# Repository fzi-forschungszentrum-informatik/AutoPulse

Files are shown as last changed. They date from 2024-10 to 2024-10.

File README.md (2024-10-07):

# AutoPulse: The ultimate do-it-yourself EMFI automation platform

This project was created researchers at KASTEL and the FZI Forschungszentrum Informatik.
In this repository, you will find the necessary files to build your own EMFI automation platform.

## [Assembly](/assembly/README.md)

This section contains the build instructions, as well as a BOM and the necessary 3D files to build your own EMFI automation platform.
As a note, these instruction are heavily reliant on the use of a specific 3D printer, the Ender 3 S1.
We used this printer because it was widely available, and contains both reliable as well as very affordable components.
It's possible to follow these instructions with a different 3D printer, but you may need to adjust the 3D files accordingly.
Take a look at these requirements when selecting a different 3D printer:

1. UART capable TMC stepper drivers.
   - The Ender 3 S1 uses TMC2208 stepper drivers, which are UART capable.
   - We needed to modify the mainboard slightly to enable UART mode.
2. Dual Z-Axis stepper motors.
   - Some Ender 3 models only have one stepper motor for the Z-Axis, which reduces the Z-Axis consistency across the X-Axis.
3. [klipper](https://klipper3d.org/) compatibility.
4. v-slot rollers on the X and Y-Axis.
   - Other solutions exhibit larger static friction, which will reduce the accuracy during small movements.

## Software

Take a look at the [Readme](pulsecontrol/README.md) in `pulsecontrol`, it details the steps required to install and configure the software part of this project.

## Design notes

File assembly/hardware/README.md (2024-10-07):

# Build Instructions

This section will guide you through the process of assembling the hardware components and the main assembly of the AutoPulse system.

## Dissabling the stock hotend

We are using parts of the stock hotend for our EMFI mount, so we need to remove the stock hotend first, if you've already installed it. If the printer is still in its stock configuration, you can skip this step, as the hotend is already removed.

#TODO Add disassembly instructions

## EMFI Mount Assembly

The EMFI mount is a simple assembly consisting of four parts: the clamp, the mounting plate, and the CR-Touch and camera extensions.
We first need to insert the heat-set inserts into each parts.

A minimum of 12 inserts are required for the assembly, but we recommend using 16 inserts for added stability and functionality.
Take a look at the images below for reference on where to insert the inserts.
Set your soldering iron to a temperature between 180-200°C and use a wide and short soldering tip push in the inserts.

### Mounting Clamp

#### Parts List

- 6x M3x6mm SHCS
- 4x M3 washer
- 12x heat-set insert (minimum 10)
- (printed) clamp

#### Assembly

Install the heat-set inserts into the clamp, take a look at the refercence images for the correct mounting positions.

Carriage Mount Sockets
Mounting Plate Sockets
CR-Touch Mount Sockets

### Mounting Plate

#### Parts List

- 4x heat-set insert (minimum 2)
- (optional) 1x M3x10mm SHCS

#### Assembly

Install the heat-set inserts into the mounting plate, take a look at the refercence images for the correct mounting positions.
The two outer inserts on the bottom of the plate are required for the PCB camera extension, the two other inserts are optional, one is for one additional screw on the PCB camera extension, the other is for the optional M3x10mm screw we use as a zip-tie anchor.

Mounting Plate

### CR-Touch Extension

#### Models

- [Swivel](../models/Touch-Probe/Touch-Probe-Body.step)
- [Mount](../models/Touch-Probe/Touch-Probe-attachment.step)

#### Parts List

- 5x heat-set insert
- 2x M3x6mm SHCS
- 3x M3x10mm SHCS
- 1x M4x16mm SHCS
- 4x 6x3mm Neodym Magnet 

#### Assembly

Install the heat-set inserts into the CR-Touch swivel and mount, take a look at the refercence images for the correct positions.
CR-Touch Swivel HEAT-SET

Next, install the magnets into the appropriate cutouts. Make sure the magnets are aligned to attract each other, as shown in the reference image. The cutouts are tight, so no glue should be necessary to keep them in there. You might need to push them in using a screwdriver. Be carefull to not break the printed part!
CR-Touch Magnets 1
CR-Touch Magnets 2

We are now ready to attach the swivel arm to the mounting bracket. Use the M4 screw and some elbow grease. The swivel arm has enough clearance for it to freely swing around the screw as a pivot, but the mounting bracket screw-hole is designed to be self-tapped by the M4. The clearance is designed for PLA parts, so your milage may vary if you're using a different material. 
CR-Touch Pivot Screw

Now for attaching the CR-Touch. Use the M3x6mm screws to mount the probe to the swivel arm. Guide the cable through the provided hole. It's easier to keep the cable attached to the CR-Touch rather than attaching it once the probe is screwed in.
CR-Touch Probe Attachment
CR-Touch Probe Attachment

Finally, attach the part to the mounting clamp. First insert the heat-set inserts on the front of the mounting clamp, as shown here: 
CR-Touch Mounting Holes

Then attach the part to the clamp with the M3x10mm screws.
CR-Touch Pointing Down
You should now be able to tilt the CR-Touch probe out of the way after the initial sequence is done, which helps with clearance on some target boards.
CR-Touch Tilted Away

### PCB Camera Extension

#TODO Add parts list
#TODO Add assembly instructions

### Probe Camera

For the final assembly of the probe camera, we it's best to have the Raspberry Pi already set-up, as well as all components already connected.
We will then open up the camera view, which simplifies the final alignment of the camera.

#TODO Add parts list
#TODO Add assembly instructions

#### Replacing the stock leveling screws

The default leveling screws are too large for the new probe camera module and will interfere with the movement of the carriage. We have designed a simple replacement part that is easy to print and install.
Screws
Our part uses the same threaded insert as the stock screws. Simply use a soldering iron to heat the insert, pushing it out of the stock screw, and insert it into the new part.
We recommend to only replace the screws on the left side of the printer, as the right side is not impacted by our probe camera module.

## Assembly

#### Parts List

- 6x M3x6mm SHCS
- 4x M3 washer
- 1x stock Creality PCB breakout board
- 1x assembled EMFI mount

#### Assembly

Use two of the M3x6mm screws to attach the PCB breakout board to the mounting assembly.
Place two washers each between the printed part and the PCB breakout board.
Be careful when screwing in the screws, the mounting tabs are fragile.

Line up the assembled EMFI mount with the printer carriate, then screw in the M3x6mm screws.

## Electronics

**WARNING**: The following steps require you to open the electronics compartment of the printer. This will void your warranty. We are not responsible for any damage caused to your printer. If you are not comfortable with these steps, please ask for help from someone who is. Keep the printer unplugged while performing these steps.

### Opening the electronics compartment

1. Lay the printer on its right side. Remove the screen beforehand,
   you won't be needing it in the future.
2. Remove the tool-drawer before trying to remove the bottom panel.
3. Remove the 9 screws from the bottom panel.
4. Remove the bottom panel. Carefully detach the cooling fan cable from the control board before removing the panel completely.

### (Optional) Adding UART support for the TMC2208 stepper drivers

This step is optional, but highly recommended. It will enable UART for the stepper drivers, allowing for higher accuracy and quieter operation.
If you want to do this, follow the instructions in the [Enabling UART for the TMC2208 Stepper Drivers](#part-99999-optional-enabling-uart-for-the-tmc2208-stepper-drivers) section, then return here.
You can also do this step after the initial setup, but it is easier to do it now, while the electronics compartment is already open.

### Wiring

1. Locate the heated-bed cable and thermistor cable. Both are located on the left of the board, labeled as "BED" and "BED TEM" respectively. Take a look at our [wiring diagram](img/wiring-diagram.png) for reference.
2. Use your fingers to remove the hot-glue from the heated-bed cable and the thermistor cable. Try to avoid using metal tools for removing the hot-glue, as you might damage the PCB.
3. Unscrew the terminals of the heated-bed cable and the thermistor cable. You can use a flat-head screwdriver for this.
4. Insert the cables for the probe-LEDs into the terminals previously used for the heated-bed.
   Keep the polarity in mind.
   Test this before before closing the electronics compartment.
5. Use the cable-clip at the top of the aluminium extrusion to secure LED cable.
6. (Optional) While the panel is open, remove the bottom cable clip which usually holds the rainbow cable. Secure the end with the tape that's already holding it down.
7. Note down the exact chip on the control board. We will need this in the future. It should be one of either `STM32F401` or `STM32F103`.
8. Replace the bottom panel and secure it with the 9 screws. Keep in mind to reattach the cooling fan cable to the control board.

### Raspberry Pi

#### Power Supply

We are using the official Raspberry Pi power supply, but it is entirely possible to use one of these [img/variable-power-supply.jpg](variable power supplies) instead. The official power supply is rated at 5.1V and 5.0A. The power supply should be connected to the USB-C port on the Raspberry Pi.

As an alternative, we have also tested the Raspberry Pi with a cheap variable power supply.
This has the advantage of being able to power the Pi with the 24V power supply of the printer, requiring one less power outlet.
The power supply should be connected to the GPIO pins on the Raspberry Pi.
The positive wire should be connected to pin 2 and the negative wire should be connected to pin 6.

#### CSI Camera Cables

Next, you should connect the CSI camera cables to the Raspberry Pi.
The camera cables should be connected to the CSI port on the Raspberry Pi.
The camera cables should be connected to the Raspberry Pi with the black side facing away from the Ethernet port.
The order of the cameras doesn't matter, just route them as fits best with the physical layout of your components.
You can verify both cameras work by running `libcamera-hello -n` in the command line.
There will be two outputs of `Registered camera`, each providing a path to `/dev/media{0,1,2,3}`.
All cameras should be detected out of the box when using the default raspbian image.
Try rebooting you can't connect to the cameras.
Never unplug the cameras while the Raspberry Pi is powered on.
The metal contacts on the ribbon cable can short something during unplugging, which could damage the Raspberry Pi or the Cameras.

#### Connecting the Raspberry Pi to the Printer

Use a USB-A to USB-C cable to connect the Raspberry Pi to the printer. The USB-A side should be connected to the Raspberry Pi and the USB-C side should be connected to the printer.

## Installing Klipper

### Part 0: Installing Docker

We like to use the `printd` service to manage the `klipper` configuration. This will use marginally more resources than a direct deployment of klipper, but comes with advantage of simplified dependency management simple installation.
It does require a working docker installation, so we will start by setting that up.

To do this, follow the instructions at [docs.docker.com/engine/install/debian](https://docs.docker.com/engine/install/debian/#install-using-the-repository).
Then add your user to the `docker` group with `sudo usermod -aG docker $USER`.
You will need to log out and back in for this change to take effect.

### Part 1: Setting up `printd`

1. Clone the repository with `git clone https://github.com/mkuf/prind.git`.
2. Move into the directory with `cd printd`.
3. Register the alias for simplifying the following commands. Run `alias pmake="docker compose -f docker-compose.extra.make.yaml run --rm make"`.
4. Run `pmake menuconfig`.
   Use the arrow keys to navigate the TUI, use the space bar to select and deselect options, and use the enter key to enter sub-menus.
5. Select `Enable extra low-level configuration options`
6. Select `STMMicroelectronics STM32` as your microcontroller architecture.
7. The processor model is the model number you have noted down in the wiring step.
8. If you have the `STM32F401`, select the `64KiB bootloader` offset. If you have the `STM32F103`, select the `28KiB bootloader` offset.
9. Press `q` to exit the menu and `y` to save the configuration.
10. Run `pmake` to build the firmware.
11. The finished firmware will be at `out/klipper.bin`.

#### Copying the configuration

The default location for the `printer.cfg` in `printd` is ... [TODO]: # Add path, update this description

## Part 2: Flashing the Mainboard

1. You should already have the `klipper.bin` from the previous step.
   - If you have the `STM32F103`, move this file to the root of the SD-card that came with the printer.
   - If you have the `STM32F401`, create a subfolder called `STM32F4_UPDATE` and move the file there.
2. With the printer turned off, insert the SD-card into the printer, then turn the printer on.
3. You'll get no feedback as to if you've been successful, but the printer should now be running Klipper.

**Note** If you want to change some settings and flash the firmware again, re-name the `*.bin` to something else. The MCU will not flash the same firmware file again if it has the same name.

Use these images to compare with your settings:

STM32F401
STM32F103

**Note** You are now ready to start using klipper. The next steps are optional, but highly recommended.

## Part 99999: (Optional) Enabling UART for the TMC2208 Stepper Drivers

The default configuration of the steppers on the Ender 3 S1 is tuned for fast and silent movements during prints. We do not care about speed or noise, we want the highest possible accuracy. To achieve this, we will need to enable UART for the TMC2208 stepper drivers.

### Removing the control board

1. Take a picture of the control board, to make reassembly easier.
2. Remove all hot-glue from the connectors, then
3. Disconnect all cables from the board.
4. Remove the five screws holding it in place.
5. Remove the board from the printer.

### Soldering the jumpers

1. Orient the board in such a way that the USB and SD-card slots are on the right side.
2. Locate the stepper drivers, they are on the top of the board, with each having a small heat sink glued to it.
   - Underneath each heat sink are multiple resistors in a row. One of these resistor pads is unpopulated, and this is where we will solder the jumper.
   - The upper pad itself is connected to the resistor to the left of it, which in turn is connected to the UART pin of the stepper driver.
   - We will use this empty pad to solder the jumper, because it gives us a larger target for our soldering iron.
3. Solder a Jumper to the upper pad of the three leftmost stepper drivers. We don't care about the extruder stepper driver, as it is not used in our device.
   - It's possible to use the extruder stepper as a backup, if one of the other steppers is damaged during our modifications.
4. Either crimp a dupont connector to the other end of the jumper, or solder it directly to one of the unused pins for the touch screen. Take a look at the pictures for reference.
5. Update the `printer.cfg` with the correct UART pins. Uncomment the `[tmc2209 stepper_{x|y|z>}` section if you used the same pins as in the pictures.
   - Pins `PB2`, `PB1` and `PA2` of the `STM32F401` are connected to the empty touchscreen-connector on the control board. We chose to use those because of them being in a straight, direct line, making it easier to attach a dupont connector to them.
   - Take a look at the data sheet of your chip if you want to use other pins. Simply use a multimeter to measure for continuity between the legs of the chip and the pins on the board to find the correct ones.
6. Continue with the instructions in the [Wiring](#wiring) section.

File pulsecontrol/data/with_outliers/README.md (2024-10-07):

# Explainations

## 0.01

### DR: Outlier at 276:

The glass measurement stick traversed past the 100mm point, which resets the device measurements from previously skipped steps

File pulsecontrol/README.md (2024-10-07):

# PulseControl

## Development

I found that using the pycharm remote interpreter is the best way to develop on the PI. This way you can use the IDE on your local machine and the code runs on the PI.
Add New Interpreter

Otherwise clone or rsync the code to the PI and run it there.
Make sure the PI has the required dependencies installed:

```bash
rye sync
```

To start the server, run:
```bash
just server-start
```
in the `pulsecontrol` directory.

To start a run with a specific configuration, run:
```bash
just init configuration/<description>/<integrator-name>.json 
just start
```
the description is a directory in the configuration directory and the integrator-name is the name of the integrator in the configuration file.
The integrator needs to have the same name as the python file in the integrators directory.

In the current case, this would be:
```bash
just init configuration/spc/bam.json 
just start
```

This will immediately start the run with the specified configuration.

To stop the server, run:
```bash
just reset
```
or stop the current run in PyCharm.

## Installation

**Note:** This is only required once, on the PI the server is going to run.
```bash
apt install libcap-dev libcamera-dev libksm++-dev libfmt-dev libdrm-dev python3-opencv
```

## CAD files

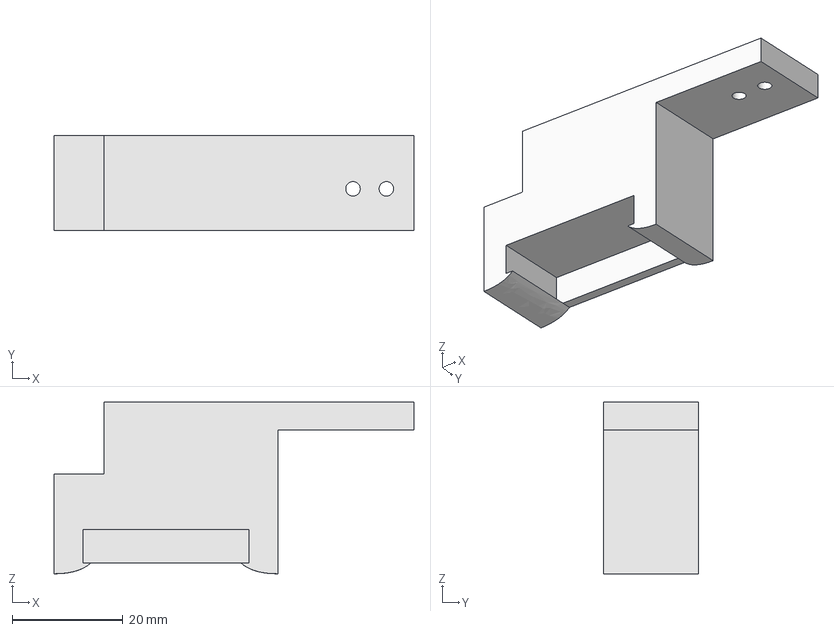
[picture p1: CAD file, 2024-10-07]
docs/assembly/models/Cable-Clip/Cable-Clip.FCStd
65.0 x 17.1 x 31.0 mm

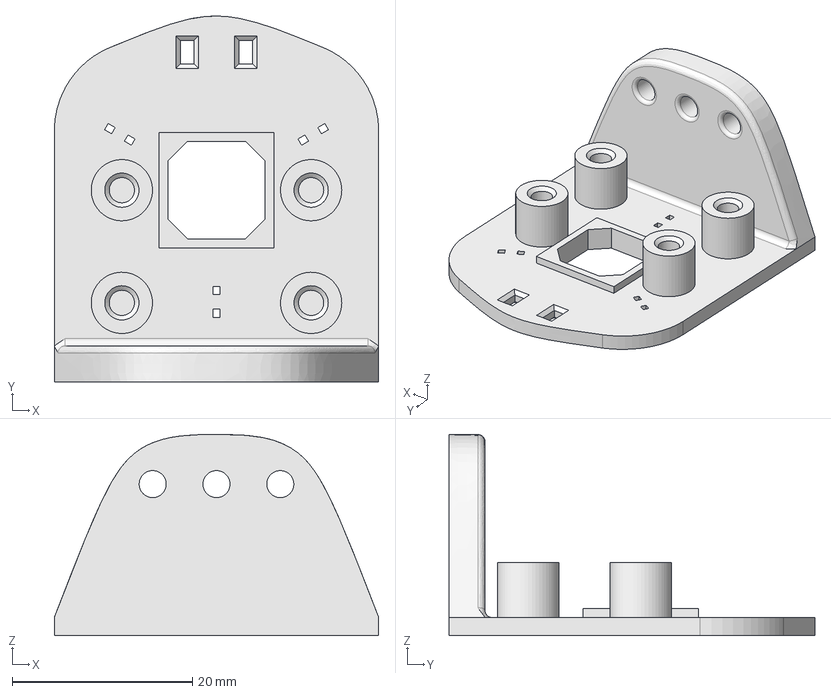
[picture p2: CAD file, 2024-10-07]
docs/assembly/models/PCB Cam/mount.FCStd
36.0 x 40.6 x 22.3 mm

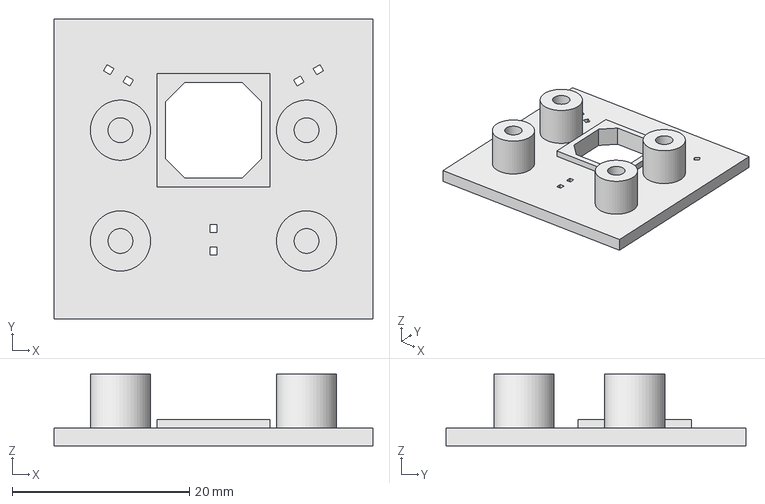
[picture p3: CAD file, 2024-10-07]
docs/assembly/models/Probe Cam/probe-cam.FCStd
36.0 x 33.8 x 8.10 mm

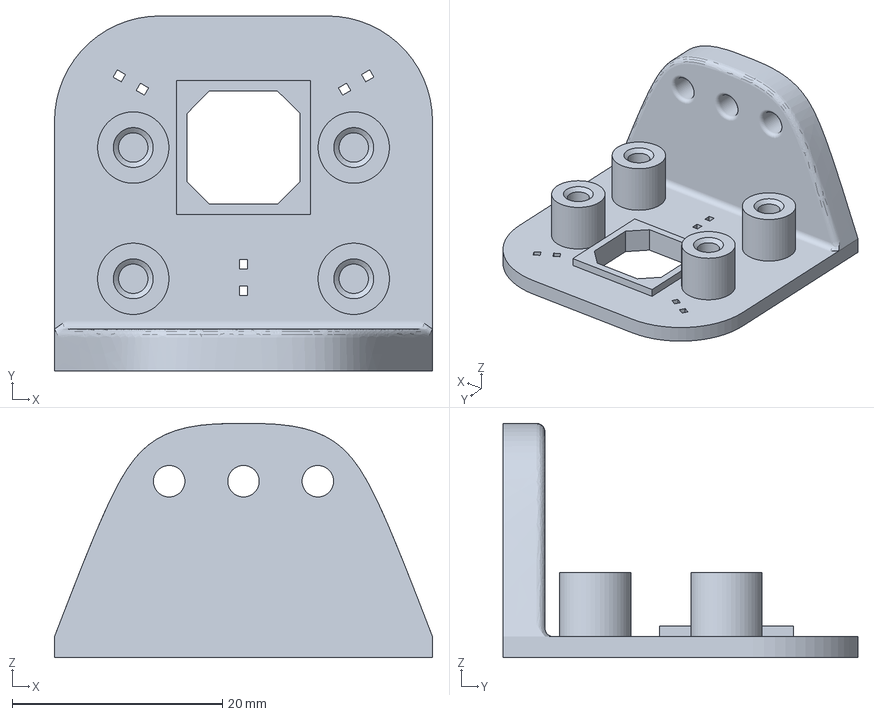
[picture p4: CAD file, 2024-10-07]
docs/assembly/models/PCB Cam/mount-BodyPad003.3mf
36.0 x 33.8 x 22.3 mm

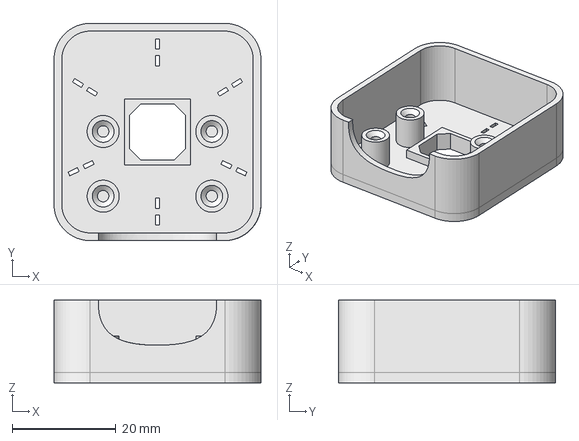
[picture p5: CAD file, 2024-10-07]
docs/assembly/models/Probe Cam/probe-cam2.FCStd
40.0 x 42.0 x 16.0 mm

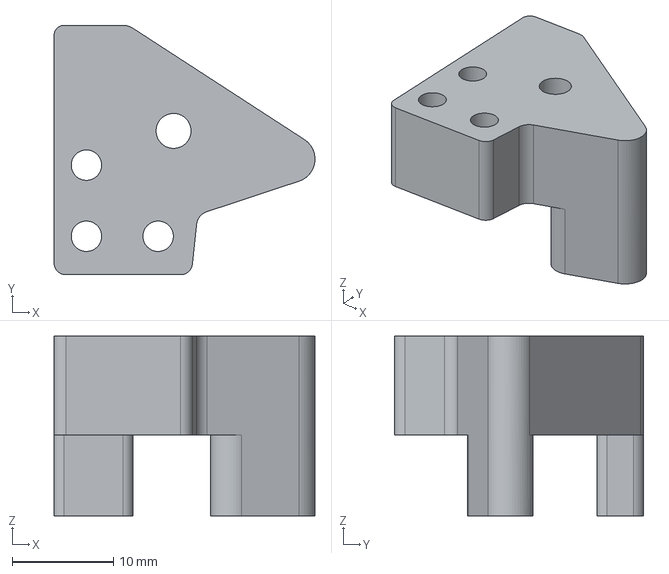
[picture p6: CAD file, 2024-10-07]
docs/assembly/models/Touch-Probe/Touch-Probe-attachment.step
25.8 x 24.6 x 17.7 mm

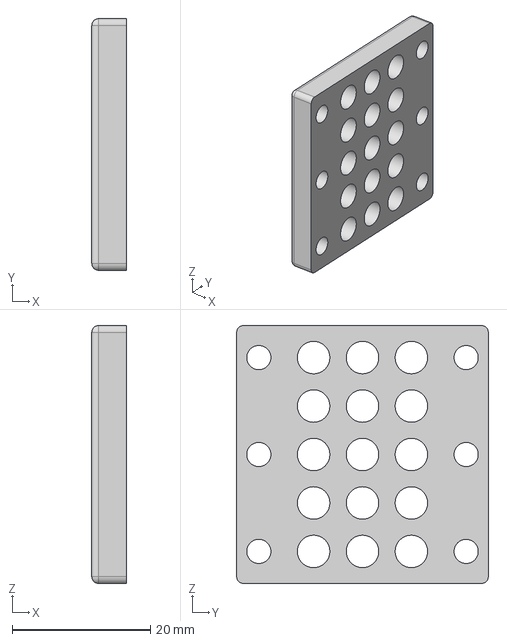
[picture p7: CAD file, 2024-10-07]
docs/assembly/models/PCB Cam/extra.FCStd
5.00 x 36.4 x 37.4 mm

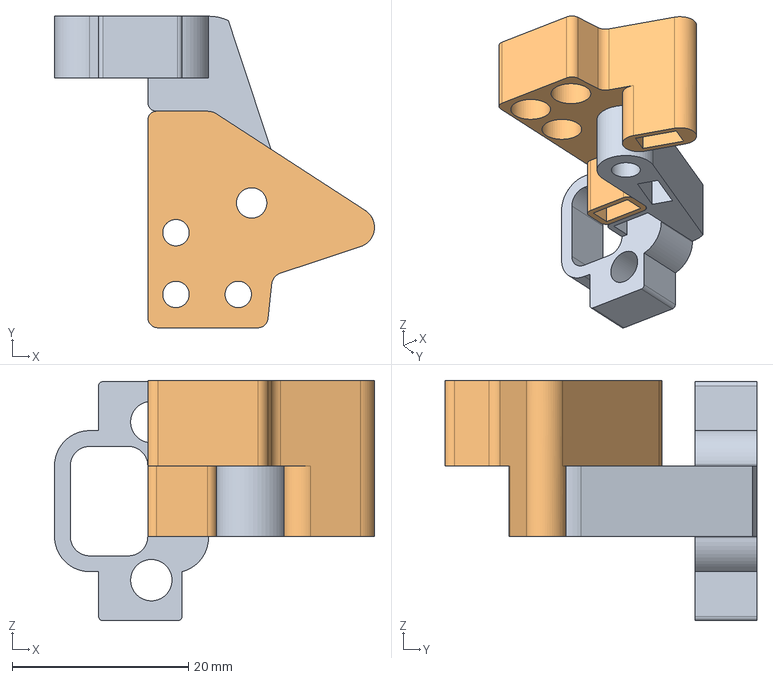
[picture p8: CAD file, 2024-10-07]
docs/assembly/models/Touch-Probe/Touch-Probe.FCStd
36.4 x 35.4 x 27.3 mm
attachment

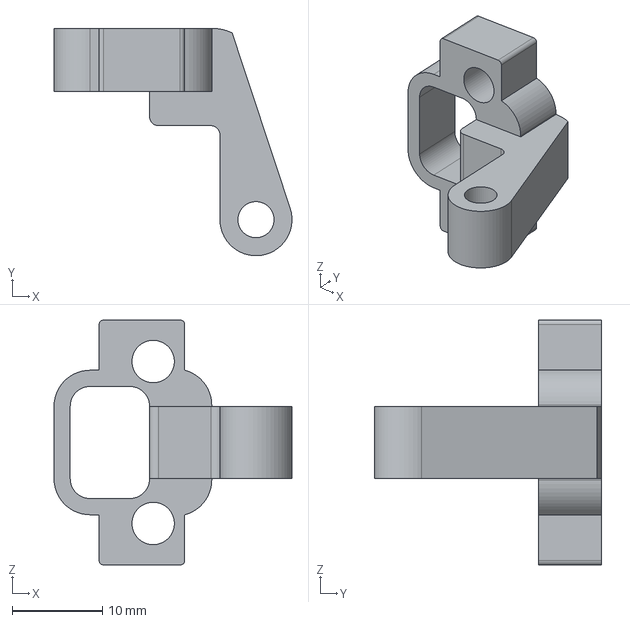
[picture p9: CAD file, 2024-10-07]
docs/assembly/models/Touch-Probe/Touch-Probe-Body.step
26.4 x 25.2 x 27.2 mm

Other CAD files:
docs/assembly/models/Touch-Probe/magnet_attachment_horizontal.FCStd
docs/assembly/models/Probe Cam/probe-cam2-BodyPocket003.3mf
docs/assembly/models/PCB Cam/mount-BodyChamfer001.step
docs/assembly/models/PCB Cam/mount-BodyChamfer001.iges

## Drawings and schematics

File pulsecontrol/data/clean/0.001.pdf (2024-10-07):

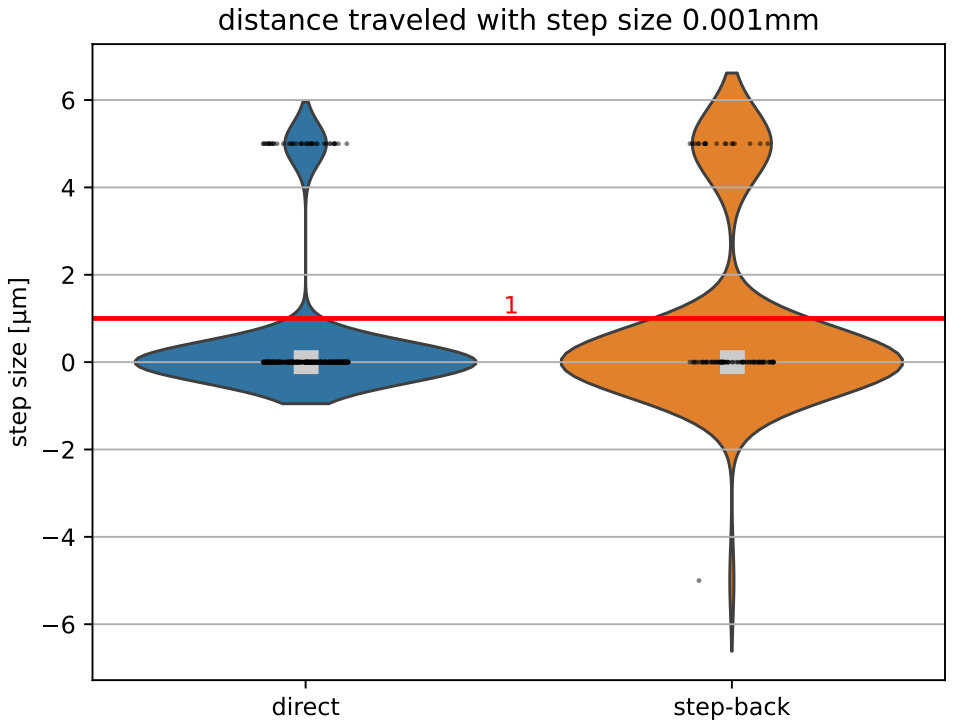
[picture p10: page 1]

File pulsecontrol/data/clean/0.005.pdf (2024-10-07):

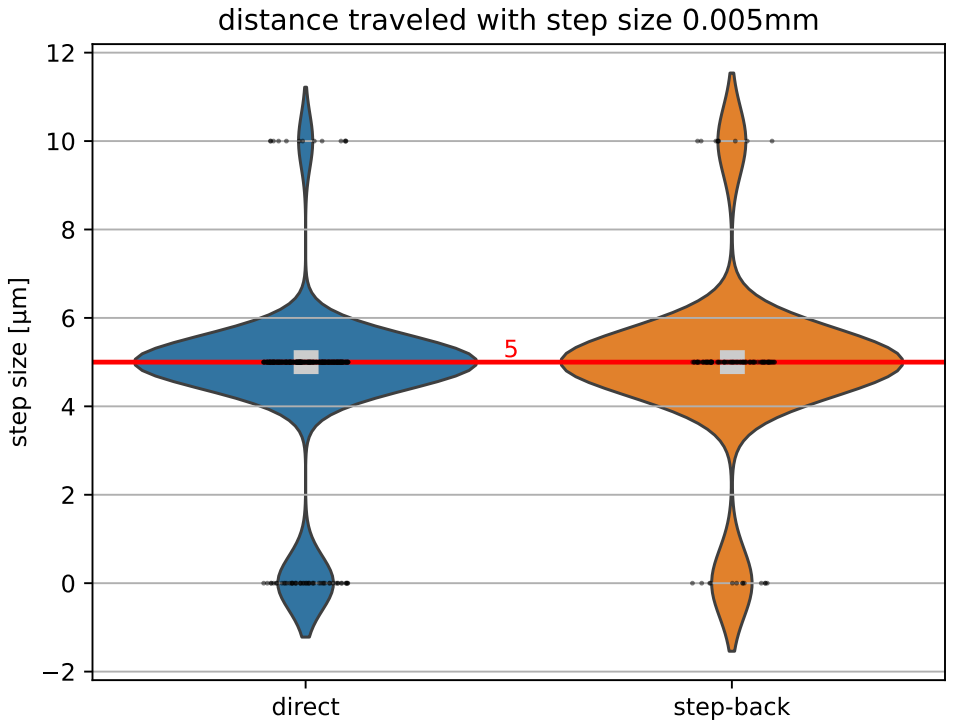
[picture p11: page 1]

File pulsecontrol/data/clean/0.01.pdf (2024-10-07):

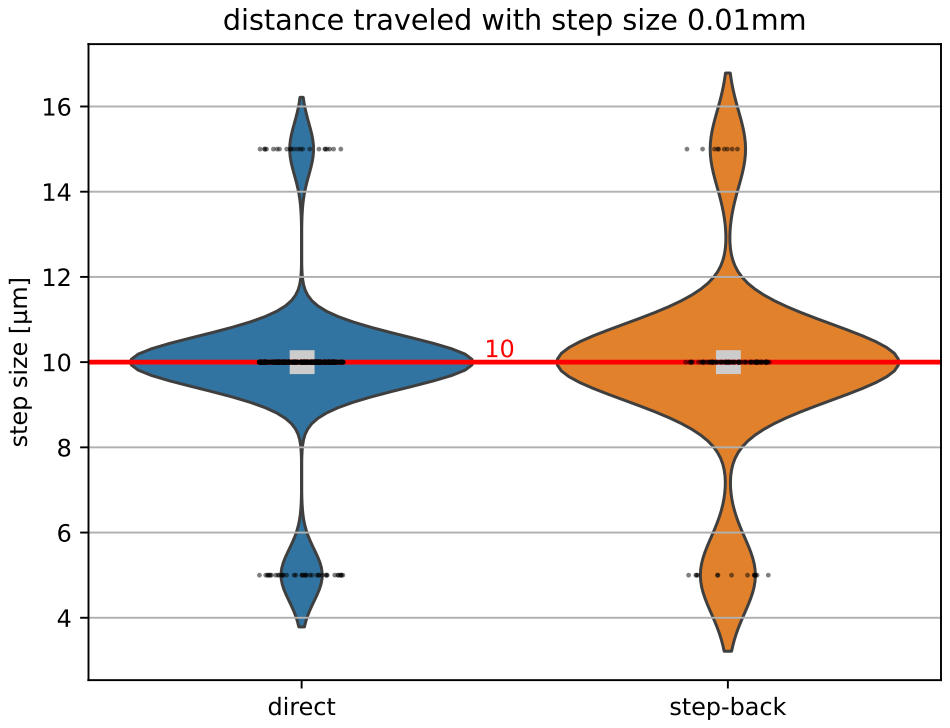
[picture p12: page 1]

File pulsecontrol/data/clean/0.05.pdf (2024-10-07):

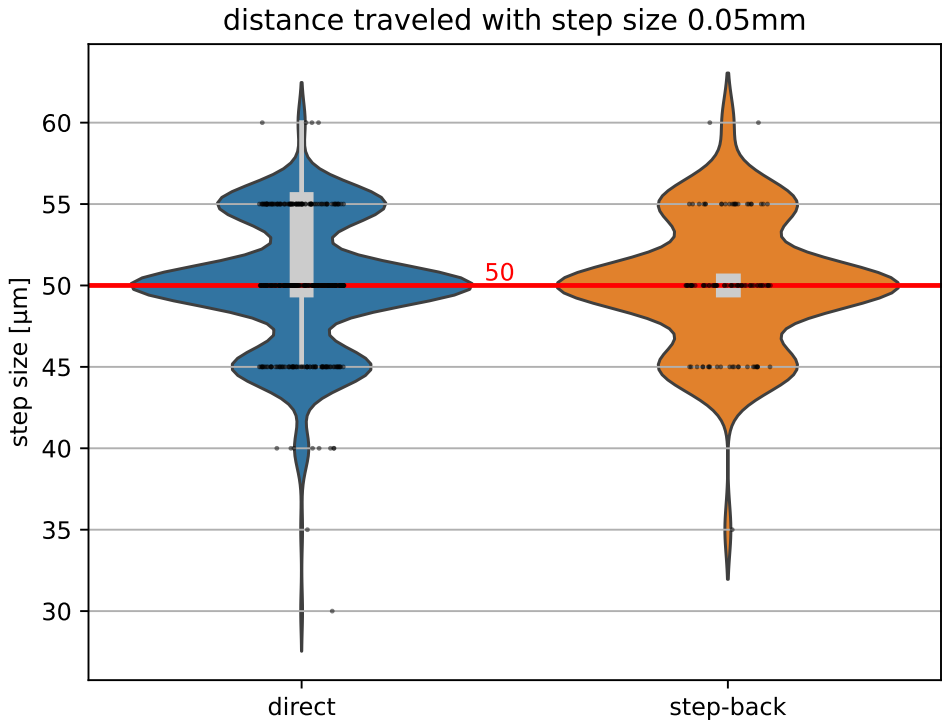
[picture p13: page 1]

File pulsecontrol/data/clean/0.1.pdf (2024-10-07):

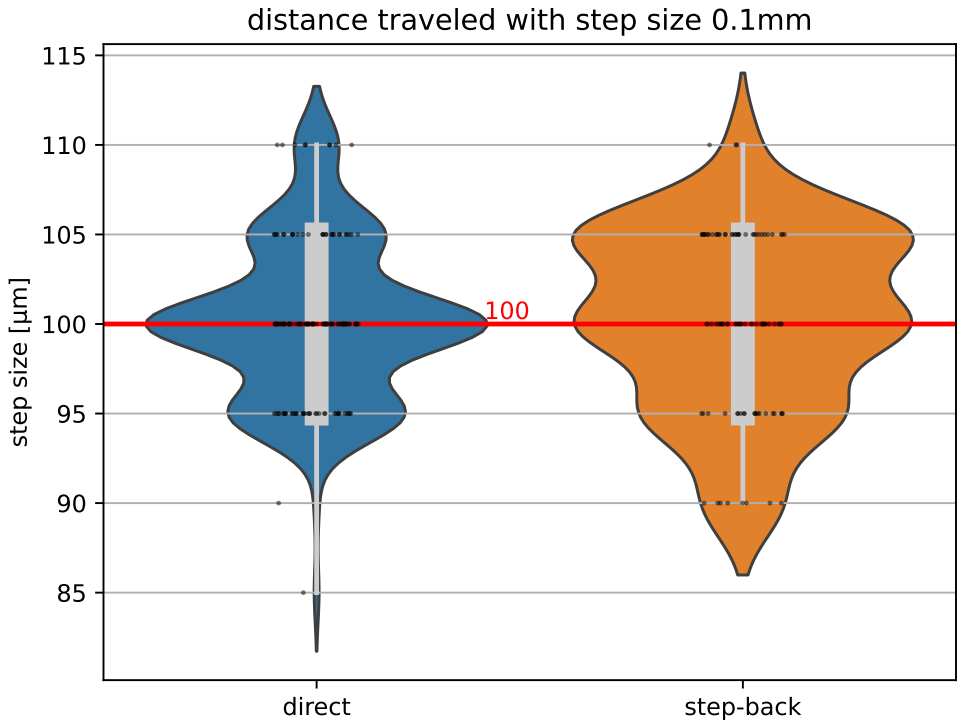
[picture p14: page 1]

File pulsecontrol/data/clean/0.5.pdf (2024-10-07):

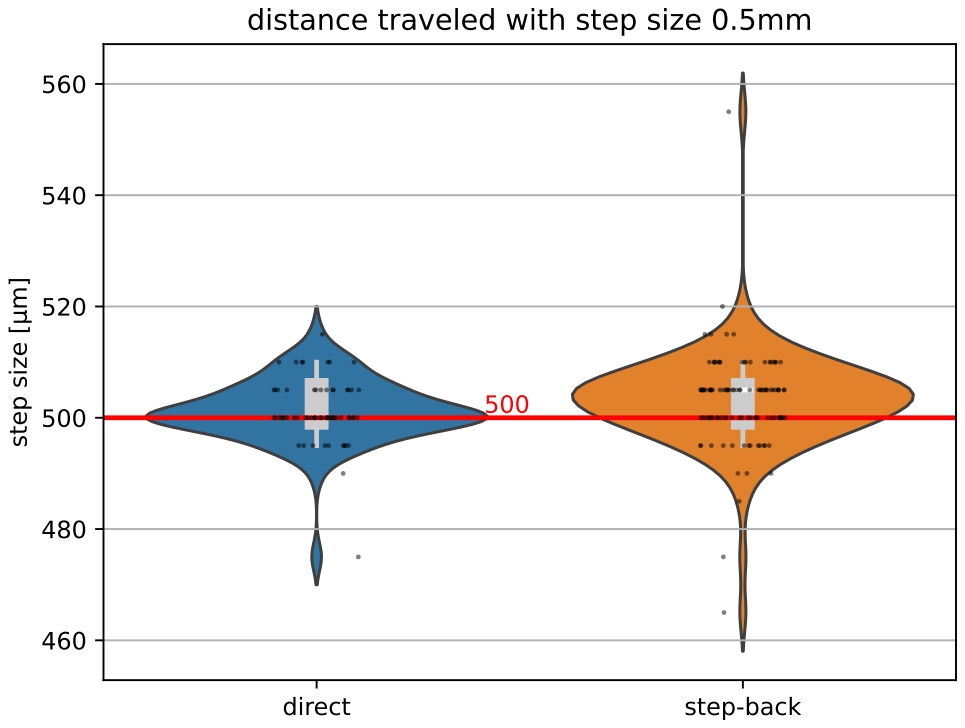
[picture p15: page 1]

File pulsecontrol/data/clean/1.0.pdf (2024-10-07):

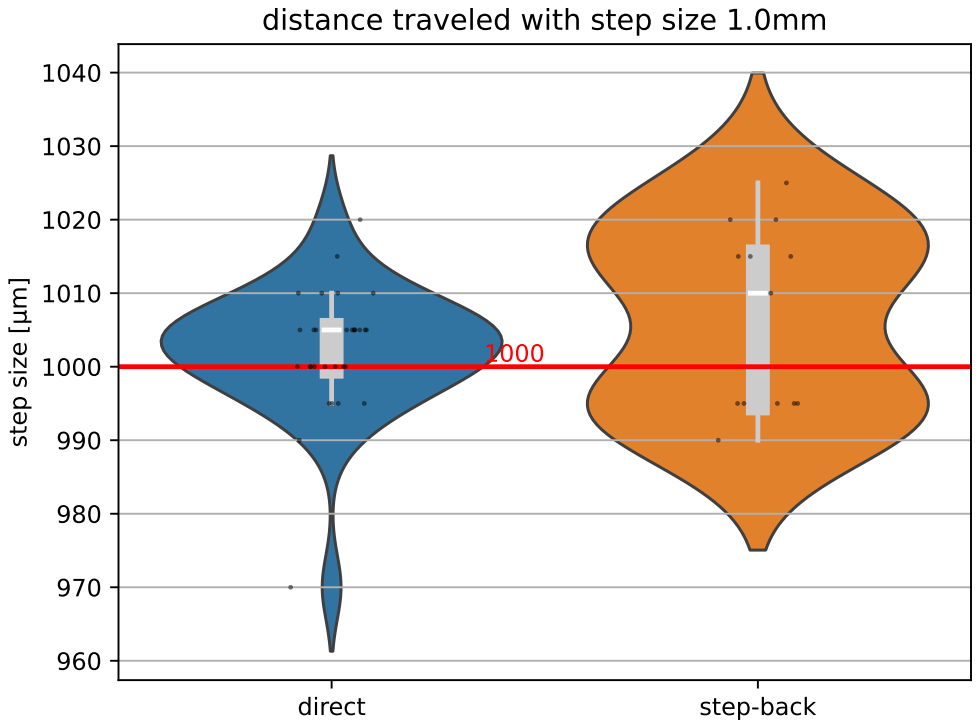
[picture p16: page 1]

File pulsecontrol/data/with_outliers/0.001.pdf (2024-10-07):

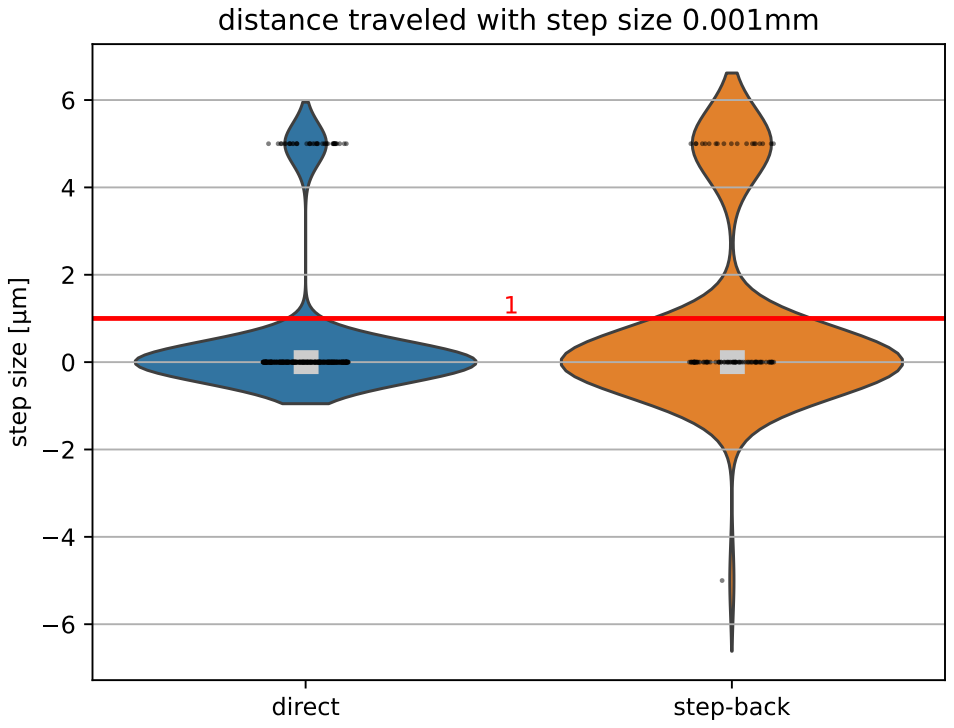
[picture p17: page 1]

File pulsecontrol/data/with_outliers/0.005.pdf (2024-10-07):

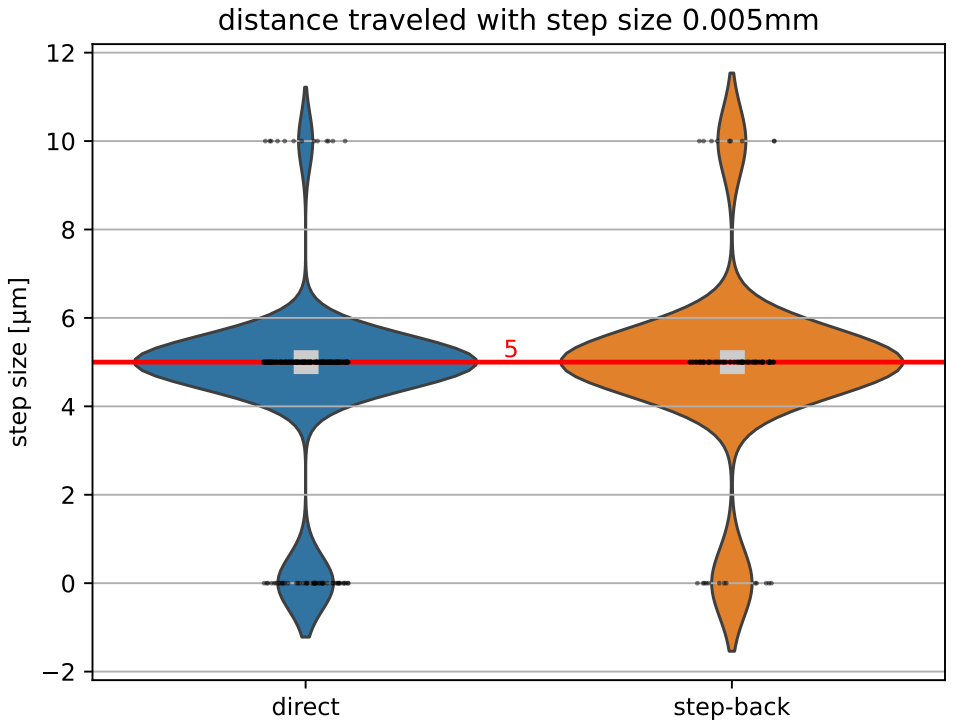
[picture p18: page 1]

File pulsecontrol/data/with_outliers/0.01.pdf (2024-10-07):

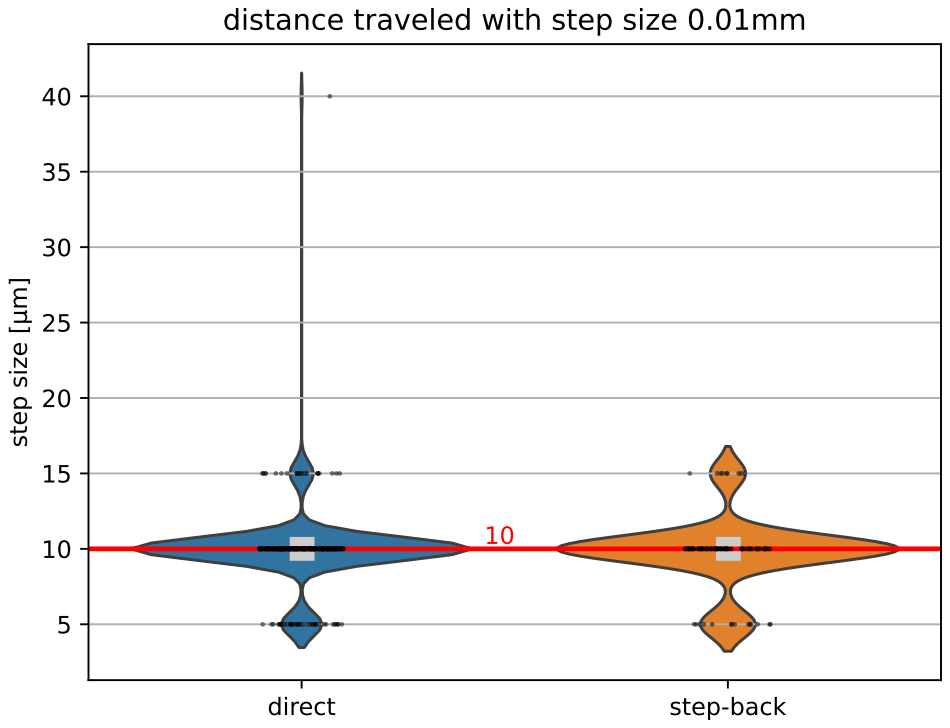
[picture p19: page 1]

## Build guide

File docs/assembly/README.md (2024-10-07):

# AutoPulse

Collected artefacts for building and controlling the AutoPulse EMFI-Station

## BOM

- 1x [Raspberry Pi 5](https://www.raspberrypi.com/products/raspberry-pi-5/)
- 1x Ender 3 S1
- 1x ChipShouter | FaultyCat | PicoEMP
- 1x Raspberry Pi Camera Module 3 Wide ([Datasheet](https://datasheets.raspberrypi.com/camera/camera-module-3-product-brief.pdf))
- 1x Raspberry Pi Camera Module 3 Wide NoIR ([Datasheet](https://datasheets.raspberrypi.com/camera/camera-module-3-product-brief.pdf))
- 2x 500mm Raspberry Pi 5 Camera Cable (the old ones are not compatible with the new connector on the Pi 5)
- 8x [White LEDs](https://www.reichelt.de/index.html?ACTION=7&LA=3&OPEN=0&INDEX=0&FILENAME=A500%2F504WC2E-W2-1PC-T.pdf) and 200 Ω resistor
- 3x [IR LEDs](https://www.mouser.com/datasheet/2/1094/MTE7110D4-1900929.pdf) and 1k Ω resistor **OR**
- 3x [White LEDs](https://www.reichelt.de/index.html?ACTION=7&LA=3&OPEN=0&INDEX=0&FILENAME=A500%2F504WC2E-W2-1PC-T.pdf) and 735 Ω resistor (approx)
- Heat-Set Inserts M3x5x4mm (Voron variant)
- various Screws (M3)
- Jumper cables
- (Optional) crimp set for Dupont connectors

## [Hardware](hardware/README.md)

## [Software-Configuration](configuration/README.md)

## [Calibration](calibration/README.md)

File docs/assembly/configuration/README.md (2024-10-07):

# Installing and configuring klipper

## Installation

## Configuration

After you've build klipper using `printd`, will have a `config` directory in the root of the `printd` directory.
This directory contains the `printer.cfg` file which is the configuration file for klipper.
This file is the single source of truth four your device, with it, you can define every possible setting and behavior of your printer.

Instead of the default file from `printd`, we will be using the configuration from this repository, located at `configuration/printd/printer.cfg`.
Either copy or link `ln -s` the file to the configuration directory of your `printd` configuration directory.

### Moonraker

We also need to adjust a setting in `moonraker.conf`, to allow our main computer to connect and send commands to klipper.

1. Open up `moonraker.conf` in the `printd/config` directory.
2. Locate the `[authorization]` section.
3. Add your computers IP address to the list of `trusted_clients`

### LEDs

We use the mainboard and existing connectors to power the two sets of LEDs we use to illuminate both the EMFI-Probe and the target MCU.
For the probe LEDs, we will be using the plug previously used for the heated bed. The pin for that is `PA7`.
The PCB LED is connected to the JST connector previously used for the parts cooling fan. The pin for that is `PA0`.
You don't need to add or adjust these values if you use the `printer.cfg` included in this repository.

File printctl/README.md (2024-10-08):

# Printer Control

We use the excellent [mkuf/prind](https://github.com/mkuf/prind) to control our printer.
Before you can start the stack, we apply an overlay to add SSL and Basic Authentication to the API and Web interface.

## Initial setup

This is a one-time setup, and you can skip this step if you have already done it.
This will clone the repository and add our overlay.
We've pinned the version to ensure compatibility.
If you need an up-to-date version, you need to manually confirm that our settings still apply.

```sh
just init
```

## Add Basic Authentication

We use the `.env` file to set the API and Web interface credentials.
Use the `htpasswd` command to generate the password hash.

```sh
echo -n 'PI_USER_PASS=' > prind/.env
echo $(htpasswd -nB pi) | sed -e s/\\$/\\$\\$/g >> prind/.env
```

This will add the user `pi` with the password you supplied.

## Start the stack

```sh
just start
```

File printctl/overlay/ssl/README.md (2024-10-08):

# Certificate Creation

This directory contains the script to generate the SSL certificates for the API and the Web interface.
You can also supply your own certificate, if your organisation provides one.

We do not advise exposing the API to the internet, even with SSL and authentication. We supply you with the tools to enable both, as it's best practice to do so, even in local networks.

## Steps to create a self-signed certificate

1. Rename the `preview.env` to `.env` and fill in the required fields.
2. Run the `create.sh` script.
3. With the default settings we applied to traefik, the certificate will automatically be picked up and served, provided you used the command `just init && just start` to set up the stack.

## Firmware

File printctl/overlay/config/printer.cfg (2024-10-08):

# This file contains pin mappings for the stock 2021 Creality Ender 3
# S1 & S1 Pro. To use this config, check the STM32 Chip on the
# Mainboard, during "make menuconfig" select accordingly either the
# STM32F103 with "28KiB bootloader" or the STM32F401 with
# "64KiB bootloader" and serial (on USART1 PA10/PA9) for both.

# For a direct serial connection, in "make menuconfig" select
# "Enable extra low-level configuration options" and  Serial
# (on USART2 PA3/PA2), which is on the 10 pin IDC cable used
# for the LCD module as follows: 3: Tx, 4: Rx, 9: GND, 10: VCC

# Flash this firmware by copying "out/klipper.bin" to a SD card and
# turning on the printer with the card inserted. The filename
# must be changed to "firmware.bin"

# With STM32F401, you might need to put "firmware.bin" in a
# folder on the SD card called "STM32F4_UPDATE" in order to flash.

# See https://github.com/Klipper3d/klipper/blob/master/docs/Config_Reference.md for a description of parameters.


################
# Basic Config #
################

[mcu]
serial: /dev/serial/by-id/usb-1a86_USB_Serial-if00-port0
restart_method: command

[printer]
kinematics: cartesian
max_velocity: 500
max_accel: 3000
max_z_velocity: 5
max_z_accel: 30
square_corner_velocity: 5.0


###################################
# Enable force move for debugging #
###################################
[force_move]
enable_force_move: True


############
# Steppers #
############
		 
[stepper_x]
step_pin: PC2
dir_pin: PB9
enable_pin: !PC3
microsteps: 256
rotation_distance: 40
endstop_pin: !PA5
position_endstop: 0
position_max: 260
homing_speed: 50

[tmc2208 stepper_x]
interpolate: false
uart_pin: PA2
run_current: 0.8
stealthchop_threshold: 0

[stepper_y]
step_pin: PB8
dir_pin: PB7
enable_pin: !PC3
microsteps: 256
rotation_distance: 40
endstop_pin: !PA6
position_endstop: 0
position_max: 245
homing_speed: 50

[tmc2208 stepper_y]
interpolate: false
uart_pin: PB2
run_current: 0.8
stealthchop_threshold: 0

[stepper_z]
step_pin: PB6
dir_pin: !PB5
enable_pin: !PC3
microsteps: 32
rotation_distance: 8
endstop_pin: probe:z_virtual_endstop
position_max: 270
position_min: -15

[tmc2208 stepper_z]
interpolate: false
uart_pin: PB1
# High current, we are driving two motors with one driver
run_current: 1.2
stealthchop_threshold: 0


#############
# LED Setup #
#############

[led probe_led]
white_pin: PA7

[led chip_led]
white_pin: PA0


##################################
# BLTouch, Safe Z Home, Bed Mesh #
##################################

[bltouch]
sensor_pin: ^PC14 
control_pin: PC13 
# offset between the chip-shouter probe mount and the BLTouch
x_offset: -22.991
y_offset: -34.579
z_offset: 0   # This offset will be overwritten by pulsecontrol
# speed:35
# samples:3
# samples_result: median
# samples_tolerance: 0.0075
# samples_tolerance_retries: 10
probe_with_touch_mode: true
# stow_on_each_sample: false
# pin_up_reports_not_triggered: True
# pin_up_touch_mode_reports_triggered: False

[safe_z_home]
# Home on the edge of the bed.
# This will protect the chipshouter from crashing into the bed if the probe fails.
home_xy_position: 258,230
speed: 50
z_hop: 40
z_hop_speed: 5

# Bed Screw
[bed_screws]
screw1: 32, 35
screw2: 205, 35
screw3: 205, 202
screw4: 32, 202
 
[screws_tilt_adjust]
screw1: 64, 76
screw1_name: front left screw
screw2: 237, 76
screw2_name: front right screw
screw3: 237, 230
screw3_name: rear right screw
screw4: 60, 230
screw4_name: rear left screw
horizontal_move_z: 10.
speed: 50.
screw_thread: CW-M3 # Use CW for Clowise and CCW for Counter Clockwise 


###########
# Sensors #
###########

[temperature_sensor Board_MCU]
sensor_type: temperature_mcu
min_temp: 0
max_temp: 100


########
# Misc #
########

[virtual_sdcard]
path: /opt/printer_data/gcodes

[display_status]

[pause_resume]

# These macros are unused
[gcode_macro PAUSE]
description: Pause the actual running print
rename_existing: PAUSE_BASE
# change this if you need more or less extrusion
variable_extrude: 1.0
gcode:
  ##### read E from pause macro #####
  {% set E = printer["gcode_macro PAUSE"].extrude|float %}
  ##### set park positon for x and y #####
  # default is your max posion from your printer.cfg
  {% set x_park = printer.toolhead.axis_maximum.x|float - 5.0 %}
  {% set y_park = printer.toolhead.axis_maximum.y|float - 5.0 %}
  ##### calculate save lift position #####
  {% set max_z = printer.toolhead.axis_maximum.z|float %}
  {% set act_z = printer.toolhead.position.z|float %}
  {% if act_z < (max_z - 2.0) %}
      {% set z_safe = 2.0 %}
  {% else %}
      {% set z_safe = max_z - act_z %}
  {% endif %}
  ##### end of definitions #####
  PAUSE_BASE
  G91
  {% if printer.extruder.can_extrude|lower == 'true' %}
    G1 E-{E} F2100
  {% else %}
    {action_respond_info("Extruder not hot enough")}
  {% endif %}
  {% if "xyz" in printer.toolhead.homed_axes %}
    G1 Z{z_safe} F900
    G90
    G1 X{x_park} Y{y_park} F6000
  {% else %}
    {action_respond_info("Printer not homed")}
  {% endif %}

[gcode_macro RESUME]
description: Resume the actual running print
rename_existing: RESUME_BASE
gcode:
  ##### read E from pause macro #####
  {% set E = printer["gcode_macro PAUSE"].extrude|float %}
  #### get VELOCITY parameter if specified ####
  {% if 'VELOCITY' in params|upper %}
    {% set get_params = ('VELOCITY=' + params.VELOCITY)  %}
  {%else %}
    {% set get_params = "" %}
  {% endif %}
  ##### end of definitions #####
  {% if printer.extruder.can_extrude|lower == 'true' %}
    G91
    G1 E{E} F2100
  {% else %}
    {action_respond_info("Extruder not hot enough")}
  {% endif %}  
  RESUME_BASE {get_params}

[gcode_macro CANCEL_PRINT]
description: Cancel the actual running print
rename_existing: CANCEL_PRINT_BASE
gcode:
  TURN_OFF_HEATERS
  CANCEL_PRINT_BASE

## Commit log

2024-10-08 chore: jpg suffic case fix
2024-10-08 feat: Add printserver control
2024-10-09 feat: add camera module for esp32 chip detection
2024-10-09 feat: Add method to get current faults
2024-10-09 feat: continue the experiment in a separate thread
2024-10-24 Fix current package versions
2025-01-21 Move assembly to docs folder, enable mkdocs
    [Cable-Clip.FCStd, Touch-Probe-Body.step, Touch-Probe-attachment.step, Touch-Probe.FCStd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]
2025-01-31 Remove tracking of ./site
    [Cable-Clip.FCStd, Touch-Probe-Body.step, Touch-Probe-attachment.step, Touch-Probe.FCStd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]
